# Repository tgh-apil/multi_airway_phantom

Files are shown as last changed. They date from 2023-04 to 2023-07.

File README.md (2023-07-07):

# Multi Airway Phantom

A multipurpose airway training phantom, created using 3D printing. This phantom can be used to practice inserting a scope into a tumorless trachea, or configured to partially compress the trachea, simulating the presence of tumors. It can also be used to practice the insertion of a tracheostomy tube. See purchasing information, how-to-use guide, and assembly instructions below.

This model was developed at the [Lynn & Arnold Irwin Advanced Perioperative Imaging Lab](https://apil.ca/), Toronto General Hospital, University Health Network.

airway assembled disassembled

## Purchasing Information

To purchase this phantom, please email <apil@uhn.ca> and a represtative will be in touch with you with more details.

**A purchased phantom contains the following**:

1. Fully assembled APIL Multi Airway Phantom
2. 3 x tumor keys (tumor tips included)

## How-to-Use Guide
#### Tumor Anatomy
* To compress the trachea, insert key(s) into the trachea cover and lock into place by twisting the key 90 degrees until it slots into the groove on the underside of the cover. 
* It may be easier to do the above step by first removing the trachea base. To do so: first detach the connector tube from the back of the head, then disconnect it from the trachea. Lift the trachea base up and out of the groove in the base plate. Insert and lock the key(s) as desired and place the trachea base back into its groove. Reattach the connector tube to the trachea, then reattach the other end to the back of the head.

#### Normal Anatomy
* Before inserting scope, ensure all tumor keys have been removed from the trachea cover so that the trachea is uncompressed.

#### Tracheostomy
* The tracheostomy portion of the phantom is independent of whether or not the tumor keys have been locked into the cover. Insert the tracheostomy tube through the opening on the phantom's neck.

## Parts, Materials & Equipment
### Parts List
> 

#### Printed Parts
* back plate — airway phantom back plate.stl/3mf
* chest wall — airway phantom chest wall.stl/3mf
* head-to-chest airway connector tube — airway phantom connector tube.stl/3mf
* head** — airway phantom head.stl/3mf
* tumor key — airway phantom key.stl/3mf
* trachea base cover — airway phantom trachea base cover.stl/3mf
* trachea base — airway phantom trachea base.stl/3mf
* trachea* — airway phantom trachea.stl/3mf
* tracheostomy port* — airway phantom tracheostomy port.stl/3mf
* tumor key tip* — airway phantom tumor tip.stl/3mf

Files are available for download [here](https://github.com/tgh-apil/multi_airway_phantom/tree/main/stl%20%26%203mf%20files).

\* ***Print these parts using flexible TPE filament. Print the rest (including the head) with a rigid plastic like PLA or PETG.***

** Headform model was modified from NIOSH National Personal Protective Technology Laboratory (NPPTL)’s ISO Digital Headforms (specifically the medium size): https://www.cdc.gov/niosh/npptl/topics/respirators/headforms/default.html

#### Other
* 4 push-in rubber bumpers — 1/2" ID, 1” high stem — https://www.mcmaster.com/9310K16/
* 3 zip ties
* 9 M4 screws (4 - 40mm long, 5 - 18mm long)
* 2 M3 screws (12mm long)

### Materials
* PLA, PETG, or a similarly rigid 3D printing filament
* TPE (flexible) filament, specifically for the trachea, tracheostomy port, and tumor key tip

### Equipment
* 3D printer (a Prusa i3 MK3 printer was used here)
* Drill 

## Assembly Instructions
1. Print out the printed components. Each part only needs to be printed once per model, except for the tumor keys and tumor key tips, which can be printed more times to create more complex tumor anatomy if desired.
2. Insert a rubber foot into each of the 4 holes on the bottom of the back plate.
3. Attach the tracheostomy port to the head with two 12mm long M3 screws.
4. Attach the head to the chest wall with four 40mm long M4 screws.
5. Insert the chest wall into the grooves along the sides of the base plate.
6. Attach the trachea base plate cover to the base plate with five 18mm long M4 screws.
7. Insert the trachea into the base plate and align it with the groove in the base plate. Secure it with 3 zip ties.
8. Insert the tip of the key into the tumor tip. If desired, configure the tumor placement by inserting and locking keys into the base plate.
9. Place the base plate into the grooves on the back plate.
10. Insert the connector tube over the open end of the trachea, then connect the connector tube with the hole in the back of the head.

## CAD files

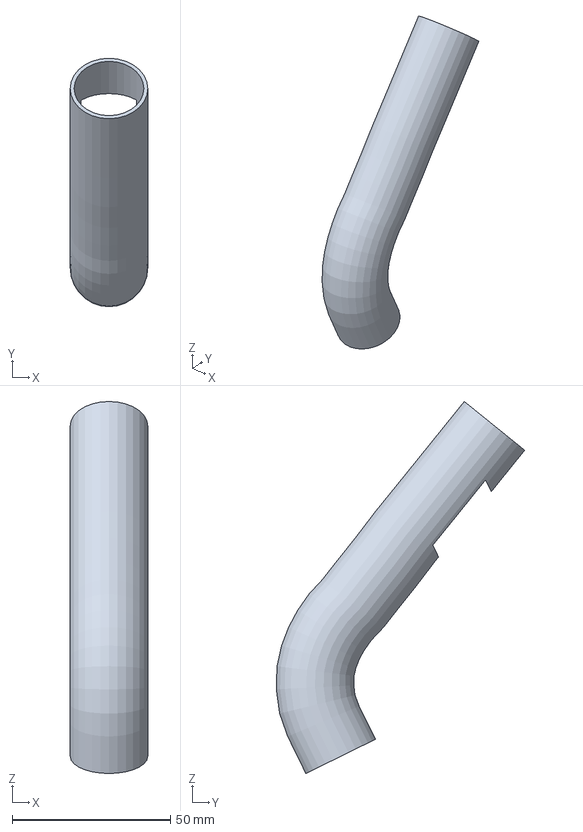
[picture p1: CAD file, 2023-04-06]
stl & 3mf files/airway phantom connector tube.3mf
24.5 x 78.4 x 117.4 mm

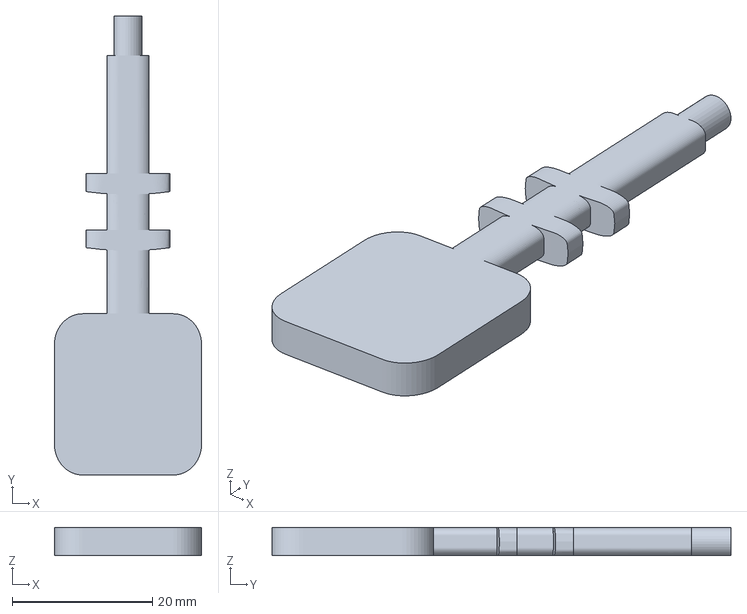
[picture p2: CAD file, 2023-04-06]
stl & 3mf files/airway phantom key.3mf
21.0 x 65.5 x 4.00 mm

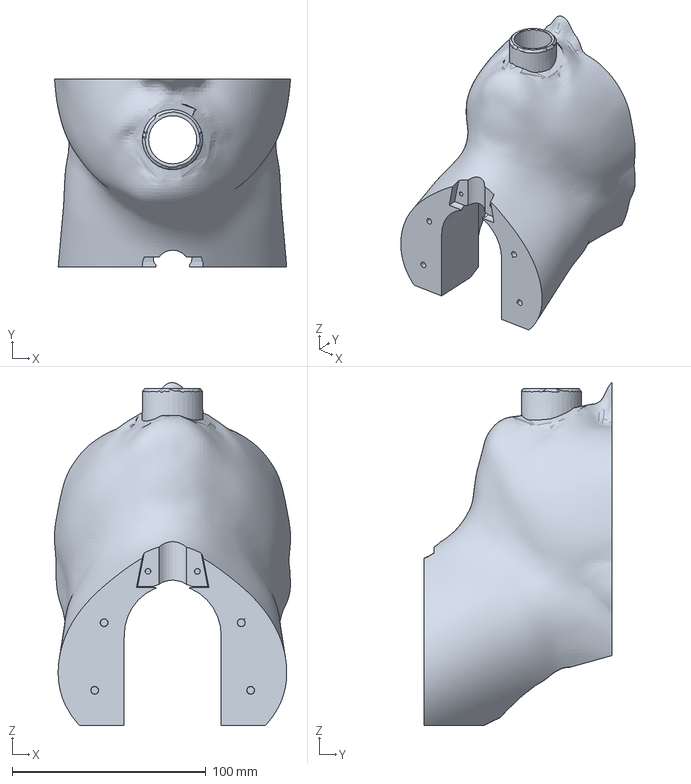
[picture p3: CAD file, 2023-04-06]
stl & 3mf files/airway phantom head.3mf
121.8 x 96.9 x 176.9 mm

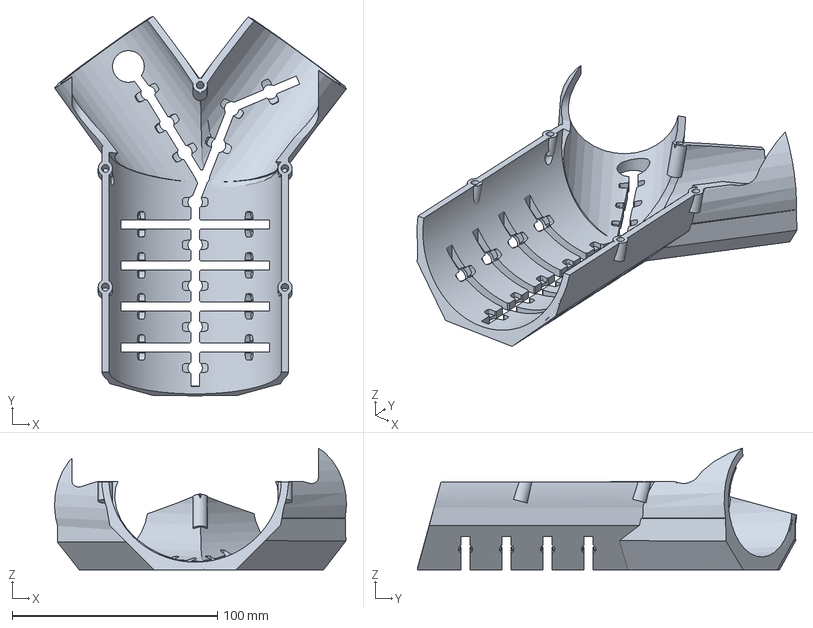
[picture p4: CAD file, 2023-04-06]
stl & 3mf files/airway phantom trachea base cover.3mf
142.3 x 185.1 x 59.3 mm

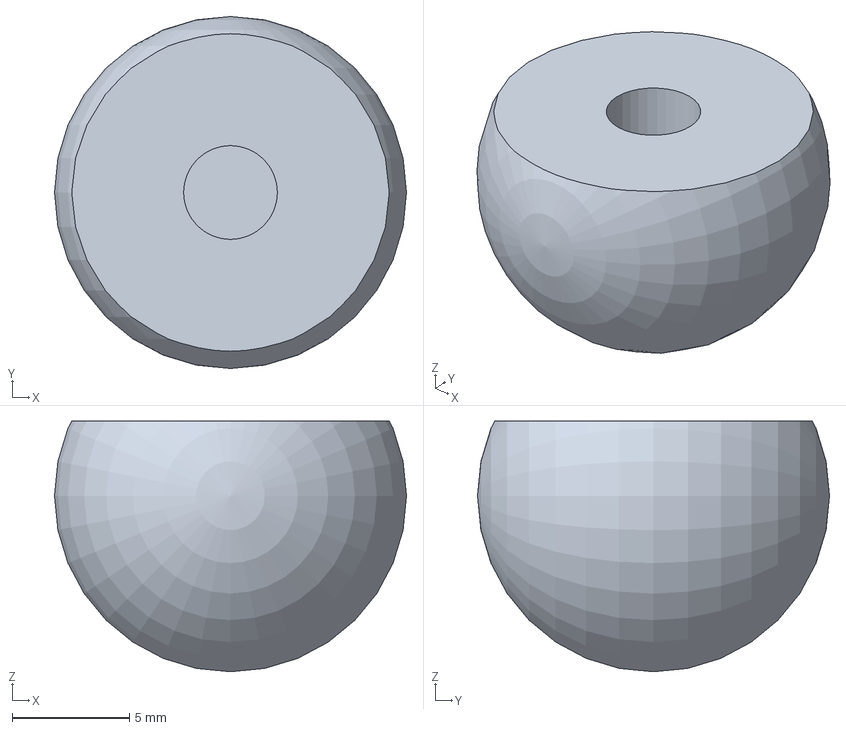
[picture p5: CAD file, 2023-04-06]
stl & 3mf files/airway phantom tumor tip.3mf
15.0 x 15.0 x 10.7 mm

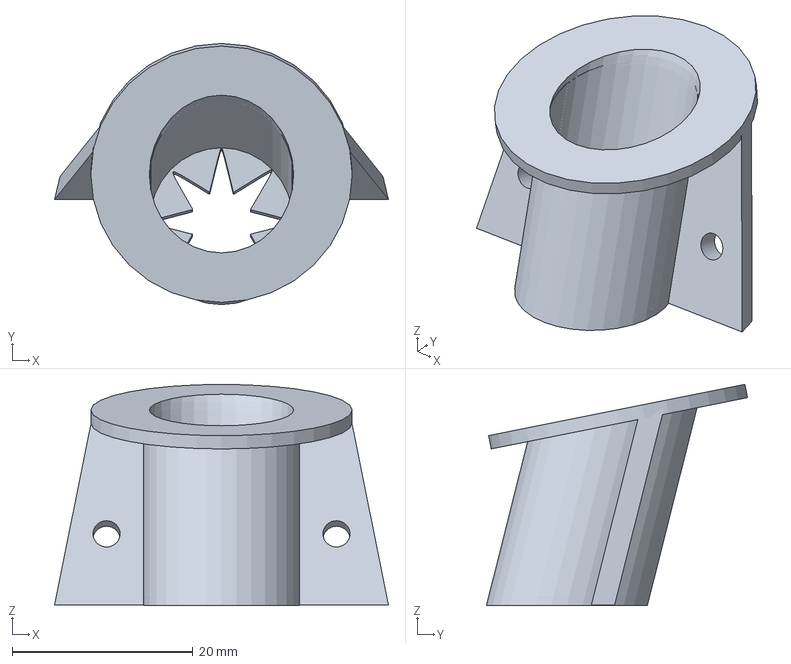
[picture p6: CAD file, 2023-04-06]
stl & 3mf files/airway phantom tracheostomy port.3mf
37.0 x 28.9 x 24.5 mm

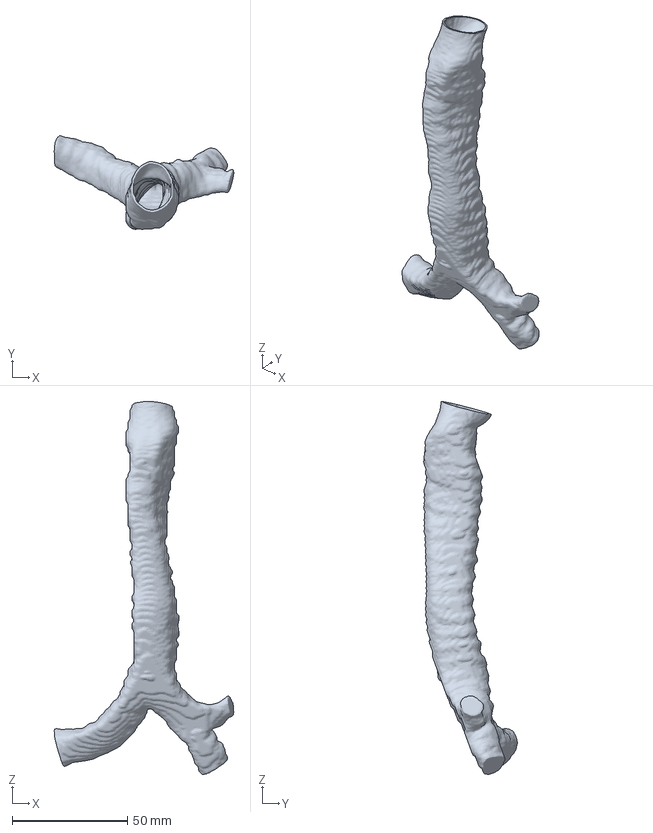
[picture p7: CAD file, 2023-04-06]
stl & 3mf files/airway phantom trachea.3mf
78.1 x 40.7 x 162.2 mm

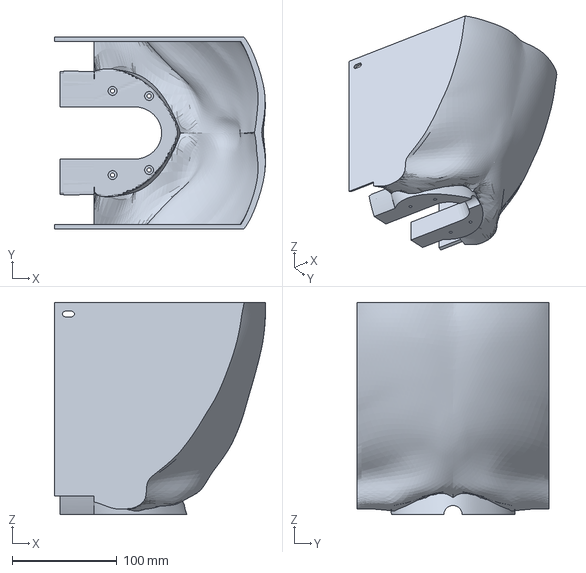
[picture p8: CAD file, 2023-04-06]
stl & 3mf files/airway phantom chest wall.3mf
201.6 x 183.3 x 202.8 mm

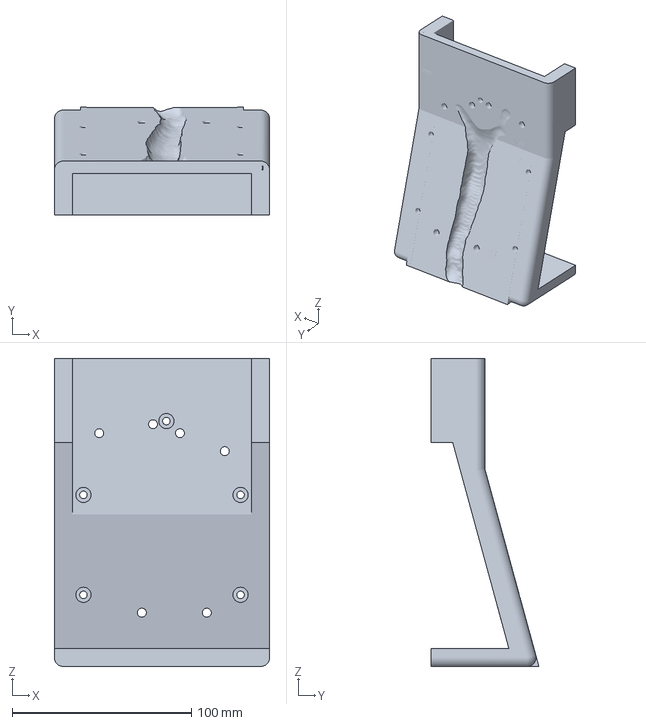
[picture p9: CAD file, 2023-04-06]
stl & 3mf files/airway phantom trachea base.3mf
120.0 x 60.1 x 171.6 mm

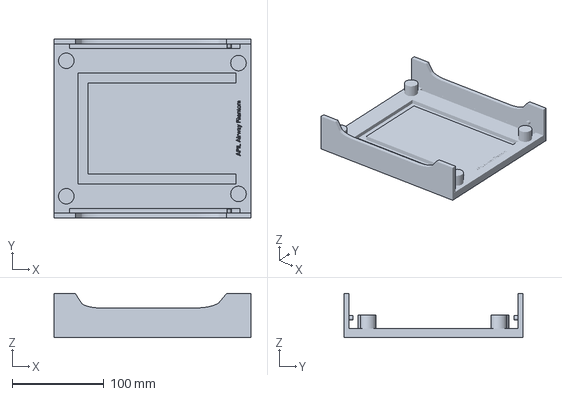
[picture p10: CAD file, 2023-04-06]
stl & 3mf files/airway phantom back plate.3mf
215.1 x 195.0 x 48.2 mm

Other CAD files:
stl & 3mf files/airway phantom back plate.stl
stl & 3mf files/airway phantom chest wall.stl
stl & 3mf files/airway phantom connector tube.stl
stl & 3mf files/airway phantom key.stl
stl & 3mf files/airway phantom trachea base cover.stl
stl & 3mf files/airway phantom trachea base.stl
stl & 3mf files/airway phantom tracheostomy port.stl
stl & 3mf files/airway phantom tumor tip.stl
